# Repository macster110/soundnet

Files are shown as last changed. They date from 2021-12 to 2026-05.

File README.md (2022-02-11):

  

# SoundNet                                            

## Introduction

Bycatch (accidental entanglement in fishing gear) is by far the greatest cause of anthropogenic mortality in toothed whales (sperm whales, dolphins, porpoise, beaked whales and river dolphins), with hundreds of thousands estimated killed each year. This enormous mortality means bycatch is an acute welfare and conservation issue which has led to large population declines and the likely extinction of at least one species and possibly two others in the near future (vaquita and Maui’s dolphin). Despite bycatch being one of the top conservation concerns for many toothed whale species, we do not know why seemingly highly intelligent animals with sophisticated sensory abilities get entangled in nets.

The reason for this knowledge gap is primarily because it's very difficult to study behaviour underwater. Video cameras cannot see more than a few meters and tagging dolphins and porpoises is very difficult and may not provide the required data. However, all toothed whales studied so far produce echolocation clicks to hunt and sense their surroundings. These clicks (and other sounds) can be detected on acoustic recorders allowing large areas of the ocean to be monitored. Whilst passive acoustic monitoring (PAM) is oten used to detect the presence and classify the species of toothed whales in an area, in certain configurations acoustic recorder can also be used to localise the position of animals. 

SoundNet is an open-source hardware and software system for localising the position of dolphins and porpoises around fishing gear, particularly focussed on gill nets (which cause the most bycatch by far). It allows dolphins and porpoises to be tracked in 3D around nets allowing both their movement and acoustic behaviour to be studied and providing insights into how animals interact with nights (and thus provide some explanation on how they might become entangled). SoundNet can be deployed from almost any fishing vessel and this provides a powerful and highly practical tool for studying the beahviour of toothed whales. 

## Concept 

SoundNet has a relatively simple concept. Two recorders which can work out the geo-referenced bearing to a received click are deployed on the headline of gill net separated by 20-50m. If two devices detect the same click, then the point at which the bearings cross is the position of the animal (see Figure 1). 

<p align="center">
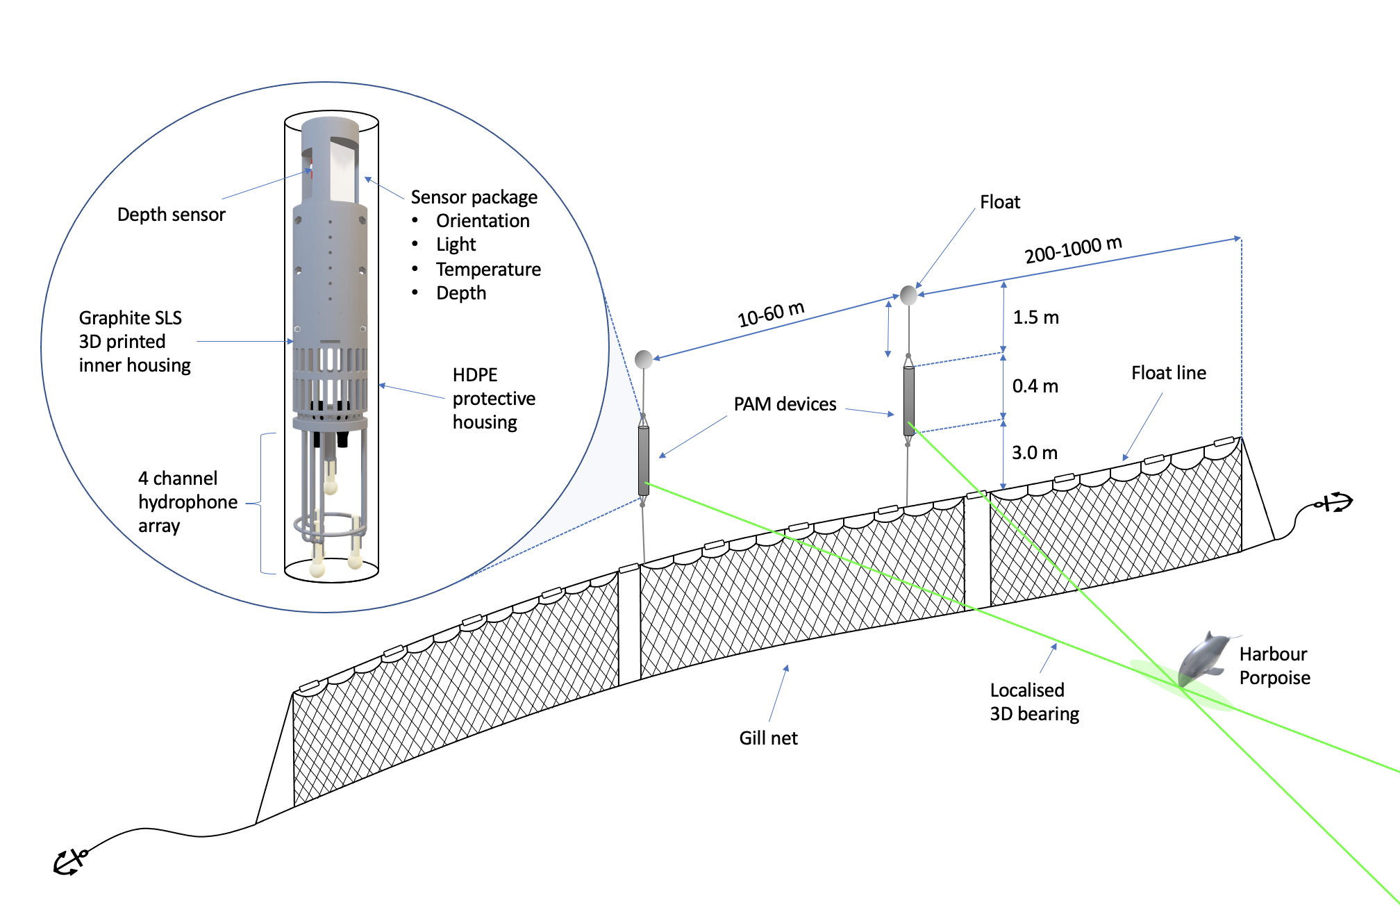
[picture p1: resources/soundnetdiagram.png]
  
</p>

_Figure 1. Diagram of the localising array (not to scale). Two recording devices were attached to the floatline of a gill net via a 3 m strop line. The recording devices were kept slightly positively buoyant using a small float, allowing them to maintain position in the water column above the float line without deforming the net. Each device contained a tetrahedral 4 element hydrophone cluster which enabled the calculation of 3D localisation vector to the source of a received sound. As a given deployment involved two devices, there was effectively an 8-channel hydrophone array mounted on the net. If both devices detected the same click, the point at which the two vectors intersected indicated the instantaneous 3D location of the animal. Animal movement patterns could then be inferred by interpolating these 3D locations._

However, whilst the concept is straightforward the implementation requires several components. 

1)	A recorder which can work out a bearing to a receiver requires multiple synchronised hydrophones. The system is based on a 4 channel SoundTrap which can be ordered from www.oceaninstrument.com. The housing section of the repository contains designs to 3D print a housing which attaches the SoundTrap and holds 4 hydrophones in a tetrahedral configuration
2)	Although multiple hydrophones can provide a bearing to an animal, the bearing needs to be georeferenced (i.e. referenced from north) for acoustic localisation to be possible. This requires an additional sensor packaged which attaches to the rear port of the SoundTrap and provides accurate 3D orientation, depth, temperature and light measurements. The sensor package section provides housing, electronic and firmware for the sensor package.
3)	Although bearings are a good way to conceptualise how the system works, they are not a great way to localise animals positions. A localization algorithm based on time delay measurements between the hydrophones and a particle filter provides much more accurate 3D tracks. The software workflow to analyse the acoustic data from SoundNet devices is detail in the analysis section.  

## Data

The resulting data from a successfully deployed system and analysis provides 3D tracks of animals which can be cross referenced with acoustic behaviour, for example tell-tale foraging buzzes. Figure 2 shows an example of 3D tracks of harbour porpoises around the net. 

<p align="center">
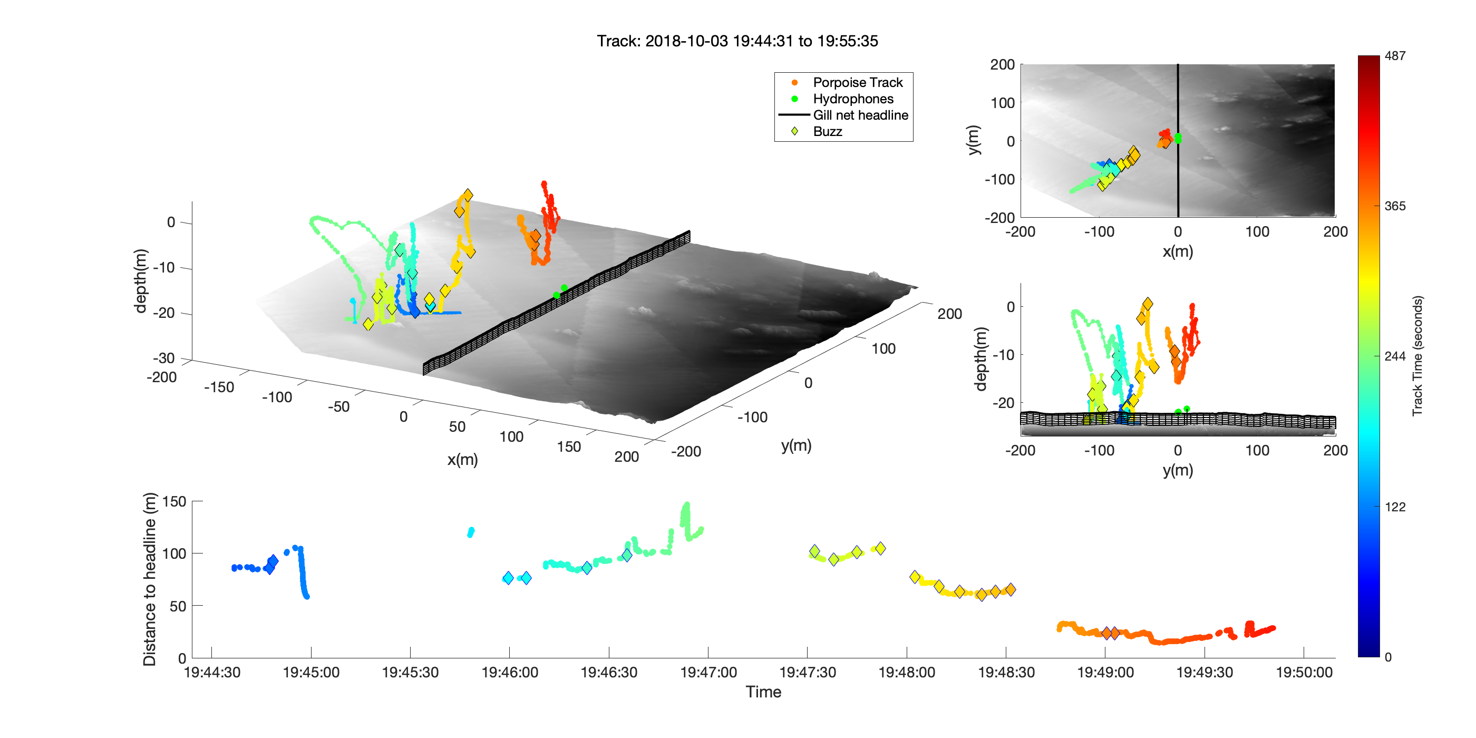
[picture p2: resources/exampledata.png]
  
</p
  
_Figure 2. Example of a 3D dive track of a single harbour porpoise where the porpoise approaches but does not come within 5 m of the gill net. A) A 3D view of the track, including bathymetry and the position of the gill net (black). Note that the gill net was assumed to be in line with the recording devices and  2m above the seabed.   B) A top-down view, and C) the depth profile along the gill net. . In this example, the porpoise dives close to the net several times producing foraging buzzes (or possibly calls) throughout the water column and towards the end of the encounter comes very close (< 5 m) to the net._

## License

This project is fully open source and any component can be used by anyone as long as it’s credited properly. We provide no guarantees and may not provide support without prior agreement.

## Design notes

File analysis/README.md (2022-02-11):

# Acoustic Analysis

SoundNet data consist of two or more (if more devices are used) sets of 4 channel wave files and sensor package files. 

## Acoustic data

### Analysis in PAMGuard

The acoustic data is analysed in PAMGuard to detect and classify possible porpoise clicks. A manual analyst then verifies detections using PAMGuard's manual annotation tools to mark out click trains and remove spurious detections (e.g. echoes). Detected clicks along with metadata such as bearing and time delays are saved to bespoke PAMGaurd files (PAMGaurd binary files) which can be imported into MATLAB using the [MATLAB to PAMGuard library](https://github.com/PAMGuard/PAMGuardMatlab) (note: you must download this library and add it to your MATLAB path). 

<p align="center">
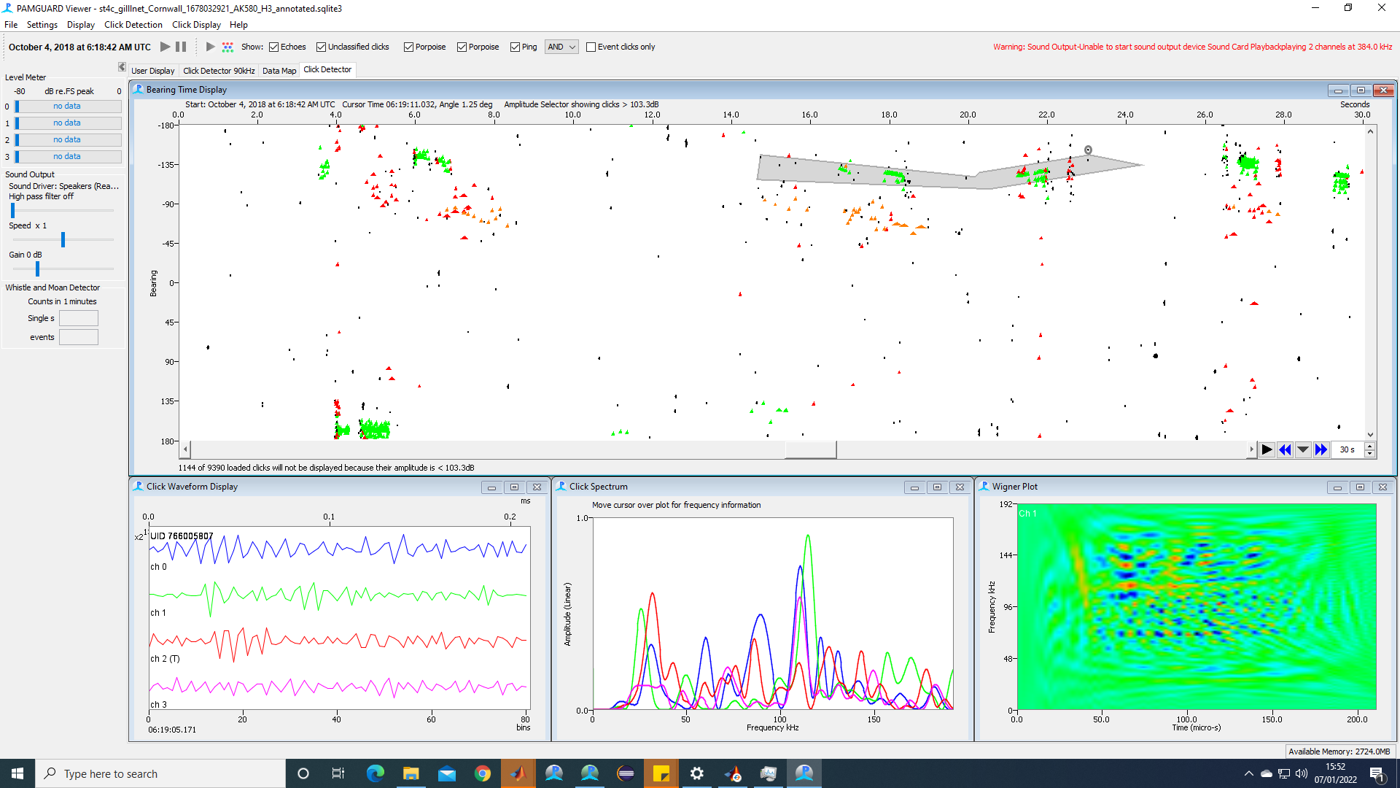
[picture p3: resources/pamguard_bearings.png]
  
</p>

_An example of clicks detected on one SoundNet device. PAMGuard automatically matched clicks on different hydrophones (on the same device, not between devices) and calculated the time delays, horizontal and vertical bearings. A manual analyst can use the slowly changes bearings to mark out click trains in the bearing time display. If more than one animal is present there will usually be concurrent separated bearing tracks._ 

### PAMGuard MATLAB library

Opening a PAMGuard binary file is straightforward. For example, a folder of binary files can be opened via

```Matlab
%the folder
folder = 'rootpath\mypamguardfolder'; 

% load clicks
clicks = loadPamguardBinaryFolder(folder, 'Click_Detector_Clicks_*.pgdf', 5);
```
This will return an array of clicks, with each element a structure containing metadata for each click such as time, waveform, time delays, bearings (if multiple hydrophones). The data can be explored in MATLAB's variable explorer or accessed via code. For example, to extract the time delay values from the first clicks in the array use 

```Matlab
timedelays = clicks(1).delays
````
The time delays are measured between all hydrophones - so for four hydrophones there are six measurements - i.e. the time delays between channels 0 - 1,  0 - 2,  0 - 3,  1 - 2,  1 - 3 and 2 - 3. 

Waveforms from a click detection can be plotted using 

```Matlab
%waveform of the first click 
wave = clicks(1).wave

tiledlayout(1,clicks(1).nChan)
for i = 1:nChan
  nexttile
  plot(wave); 
  ylabel('Amplitude (linear)')
  xlabel('Time (bins)')
end
````

<p align="center">
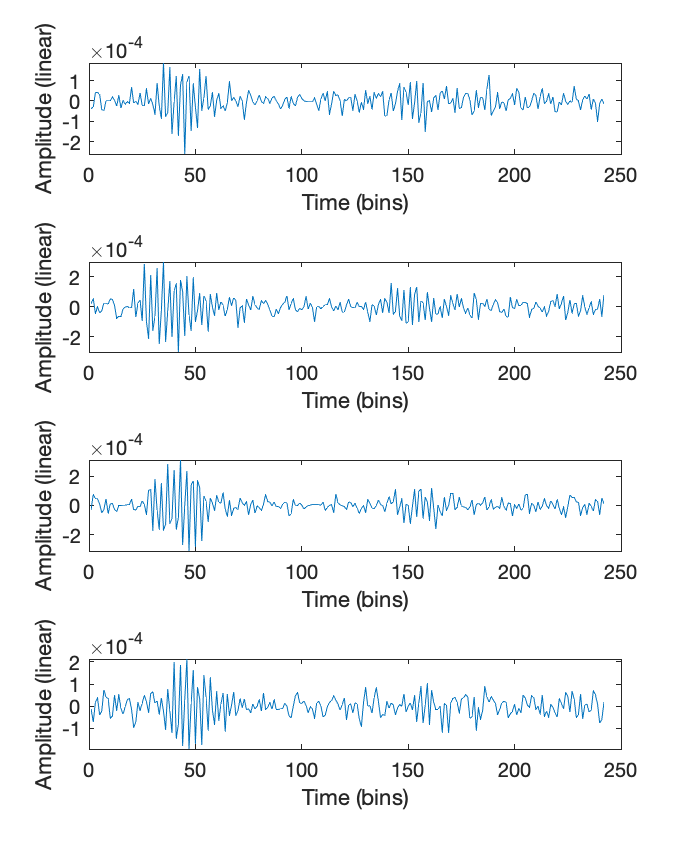
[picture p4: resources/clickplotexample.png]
  
</p>

_An example of waveforms from a single click detection imported from PAMGuard and plotted using MATLAB. Note that PAMGuard automatically matched click between hydrophones within the same SoundNet device and so one click detection contains 4 waveforms. PAMGuard also calculates the time delays between the waveforms and localised the horizontal and vertical bearing for each click_

Note that there is also a [comprehensive R library](https://github.com/TaikiSan21/PamBinaries) for PAMGuard which has like-for-like functions to the MATLAB library. 

### Importing datasets

The matlab library has several convenience functions for importing large datasets. For example,

```Matlab
% load clicks from a folder
% binaryfolder - path to the folder containinn PAMGuard binary files
clicks = loadPamguardBinaryFolder(binaryfolder, 'Click_Detector_Clicks_*.pgdf', 5);
```
will load clicks from a folder of binary files and 

```Matlab
% sqlLite_dB - path to PAMGuard's database
% binaryfolder - path to the folder containinn PAMGuard binary files
click_events = load_event_clicks( sqlLite_dB, binaryfolder)
```

will load manually annotated clicks marked out in the click detector module. 

## Sensor files

Sensor files from the sensor package attached to the SoundTrap are human readable .csv files which are saved to the SoundTrap's SD card. These can be opened using the MATLAB code in the sensor package folder. For example, to open a folder of sensor files and plot the data use

```Matlab
%folder where the csv files are located. 
folder = 'rootpath\mysensorfolder'; 

% convert csv files to one matlab struct
[sensordata] = sensorcsv2mat(csvfolder);

%plot the sensor data
plot_sensor_data(sensordataStruct); 
```

The sensordata struct contains the output from the orientation, depth, temperature, light and battery sensors on the sensor package 

<p align="center">
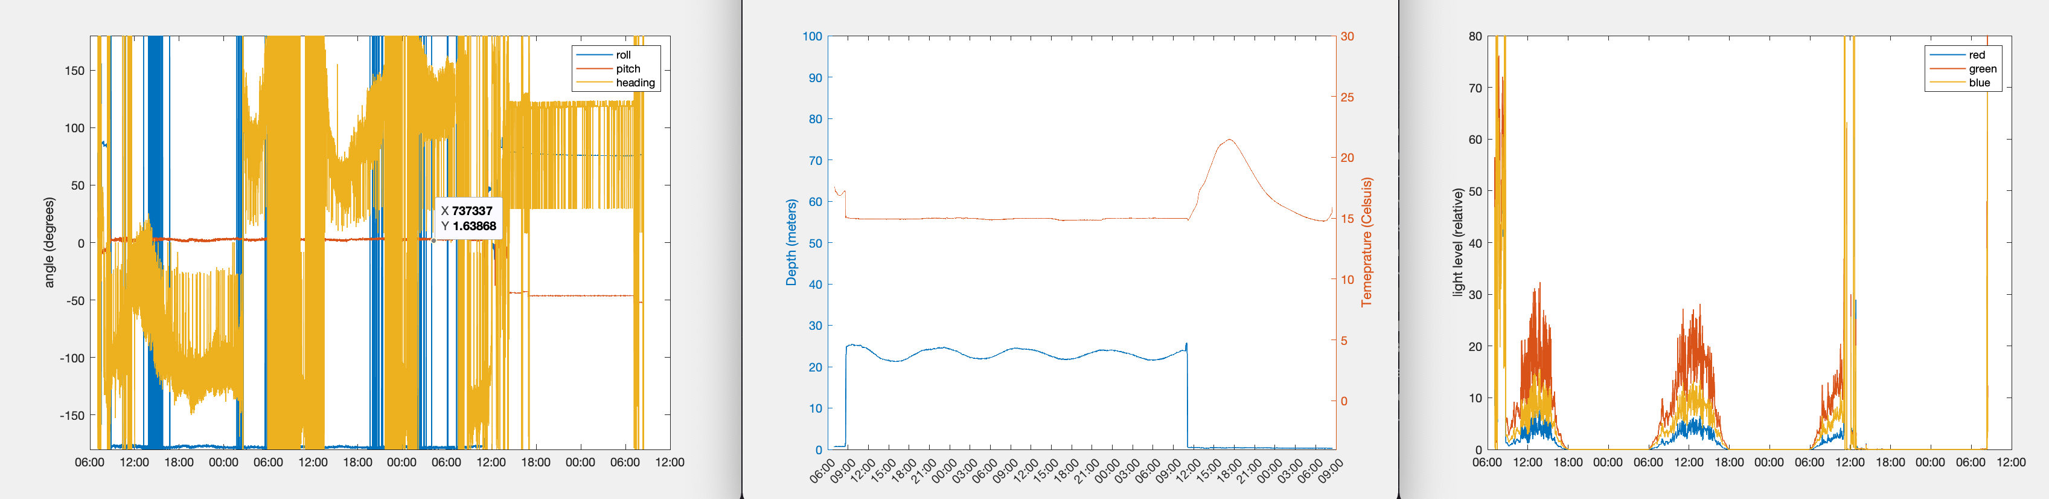
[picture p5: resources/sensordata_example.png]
  
</p>

_Example of sensor package data plotted in MATLAB._

## Geo referencing hydrophones and/or localised bearings

The sensor data is used to geo-reference clicks. The _sensordata_ folder imports .csv files and concatonates the sensor data into a single matlab structure. The functions in the _georef_ folder then combine imported click detections and the sensordata to provide geo-referenced bearings and/or hydrophone positions. aan example of how to use the functions is shown in _georef/georef_example.m_

<p align="center">
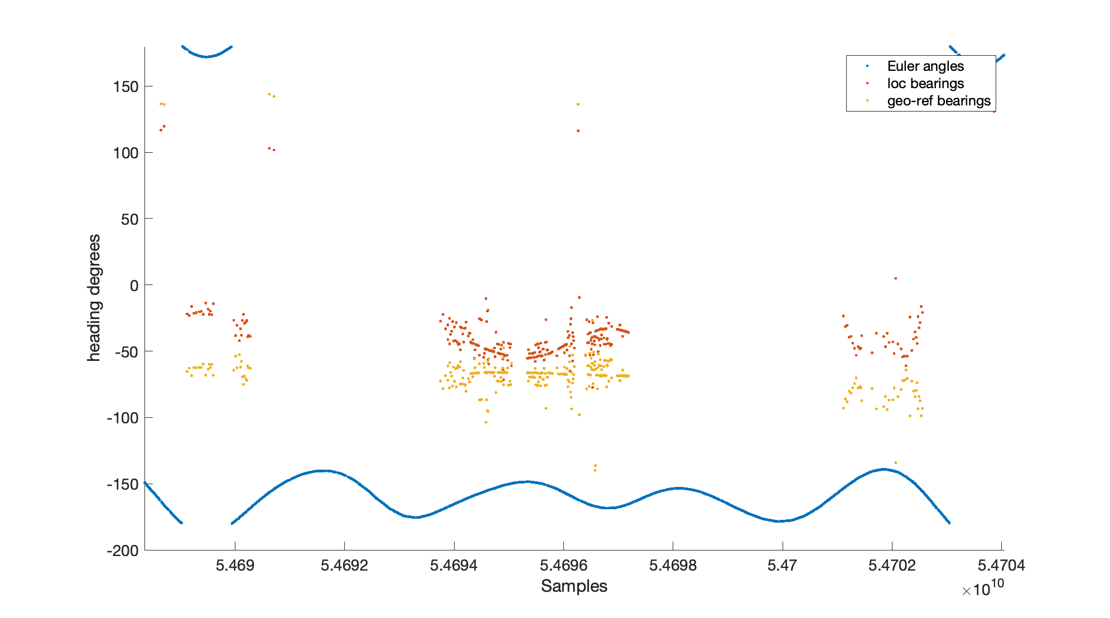
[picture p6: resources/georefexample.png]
  
</p>

_A plot of raw and georeferenced bearings to detected porpoise clicks alongisde the heading data recorded on the sensor package._

## Localisation

Localisation is performed using a particle filter. A particle filter in this context works by updated the position of a set of particles upon the detection of a click on one or more recording devices. The particles are updated based on the position of the hydrophones, the received time delays and movement model of a harbour porpoise. In this way localisation is not based on single clicks but instead on the evolved state of click trains, allowing more accurate animal tracks t be determined.

The generalised particle filter code is based on a script by  _Diego Andrés Alvarez Marín (2022). Particle filter tutorial (https://www.mathworks.com/matlabcentral/fileexchange/35468-particle-filter-tutorial), MATLAB Central File Exchange._

example_porpoise.m demonstrates how the particle filter is used in an acoustic localisation context. The script generates a simulated porpoise track, determine the time delays for clicks produced along the track and then localises the simulated track using a particle filter. 

<p align="center">
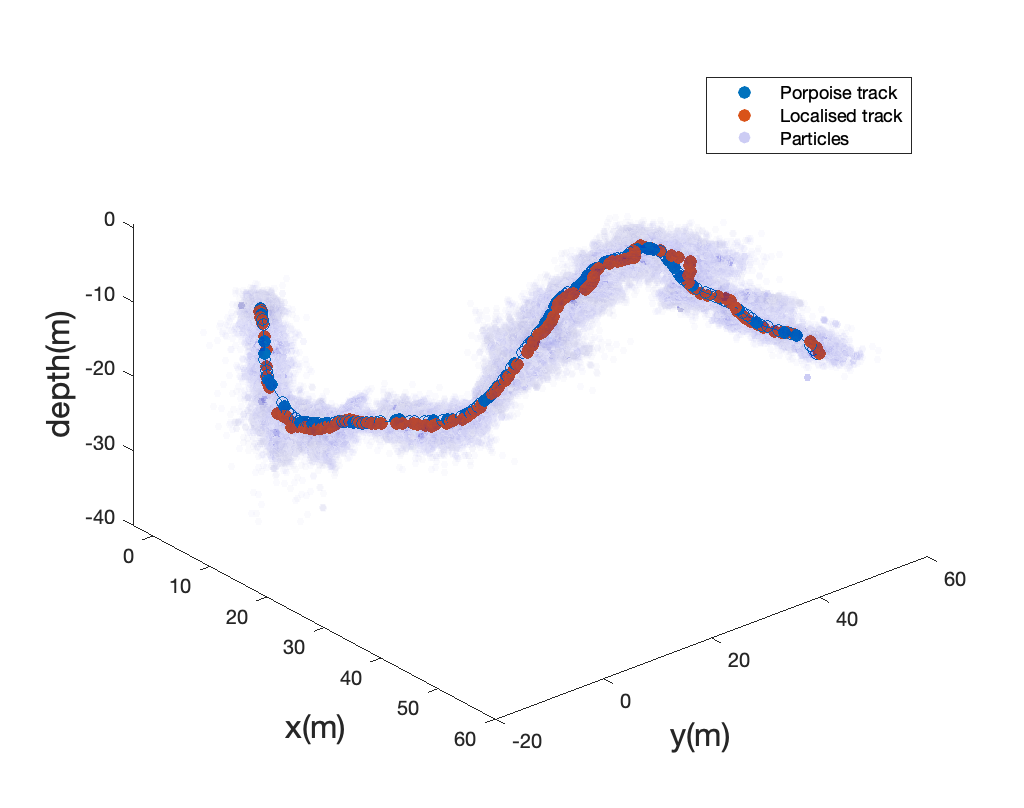
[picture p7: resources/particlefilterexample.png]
  
</p>

_Results of the particle filter using the porpoise_example.m script. The orange points are the localised positions and the blue dots the simulated animal track. The cloud of translucent points are the individual particles used by the sequential Monte Carlo process. The mean location of particles is the position of the animal and the distribution of particles is an estimate of the likely uncertainty. For example the distribution of particles in the x,y or z dimensions represents the likely error of the localisation in  x,y and z respectively._

## Data management

Data management will vary depending on the project and thus data management code is not provided here; the code provided and associated help should be considered a toolbox to construct an acoustic workflow for localisation, rather than a one-stop solution. 

However, whilst each acoustic workflow will depend on the study site, species of interest etc., they will all require some general stages as follows. 

1) Extract sounds of interest.
3) Geo reference hydrophone positons using the sensor package data.
4) Time align the SoundTraps and match clicks between different devices. 
5) Pass time aligned and geo-referenced data to the localisation algorithm to determine animal tracks.

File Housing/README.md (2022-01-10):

# Housing

Each SoundNet device consists of a 4 channel SoundTrap, a sensor pacakage and an outer housing which holds the hydrophones and sensor package in place. The outer housing is made up of three 3D printed parts which fit together over the SoundTrap and sensor package and kept in place with stainless steel bolts. 

<p align="center">
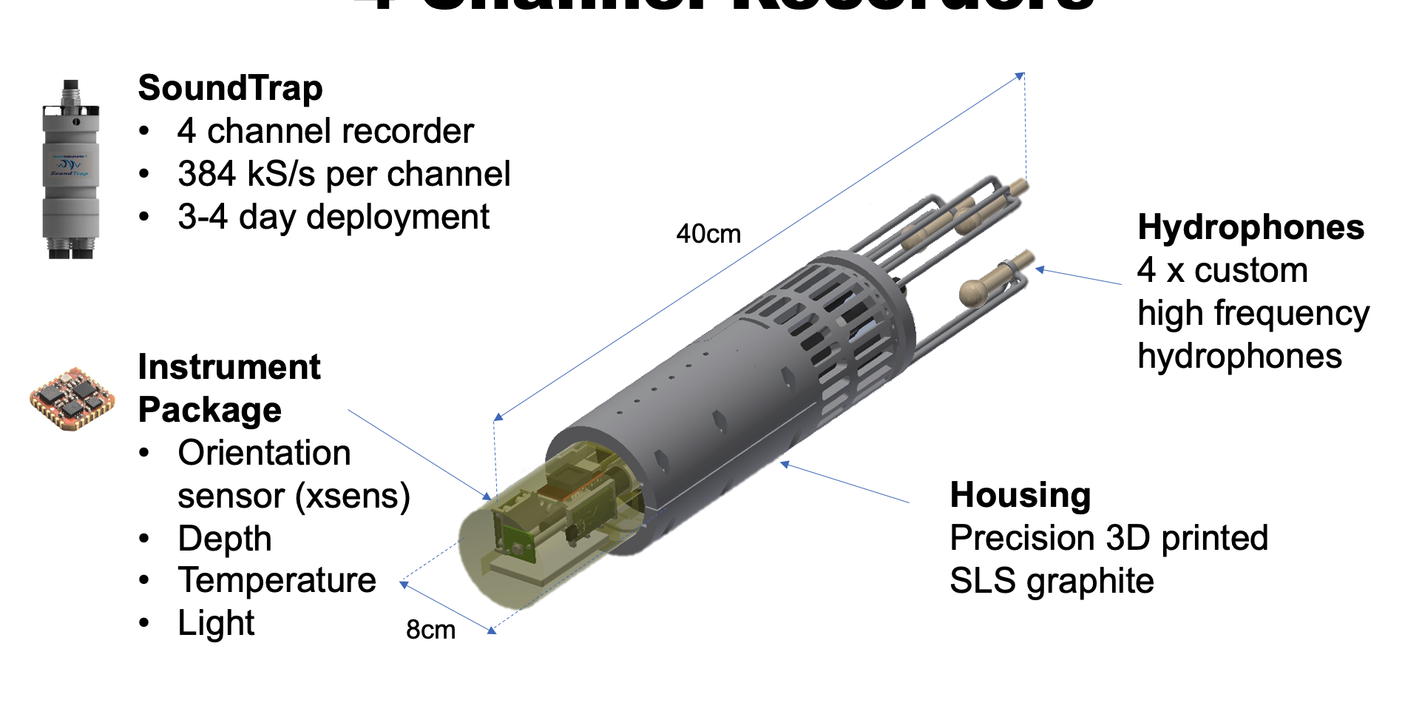
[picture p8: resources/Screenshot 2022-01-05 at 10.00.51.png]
  
</p>

_Diagram of a SoundNet device. The 3D printed housing fits over the 4 channel SoundTrap and is kept in place by stainless steel bolts._

The three .stl files here can be 3D printed easily on a local printer or using a service. The material should be rated for the marine environment and should be suitable for the intricate construction of the hydrophone frame.

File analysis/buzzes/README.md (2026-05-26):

# Buzz and call analysis 

## Importing annotated buzzes and calls
Buzz and communication call analysis was conducted by marking out rapid click sequences with an ICI <40 ms in PAMGuard. The click events were then imported into PAMGuard using the `load_event_clicks` function (Note this requires the [PAMGuard MATLAB library](https://github.com/PAMGuard/PAMGuardMatlab/releases)). 

## Plotting buzz and call contours

Once the buzzes have been imported into MATLAB, they can be saved as .mat files within the MATLAB IDE. The two .mat files for each recording device used for our analysis are included (`st13_buzzes.mat` and `st16_buzzes.mat`). Each structure contains an event and a list of click structures for each annotated click sequence in PAMGuard's standard format. More information and a tutorial on this can be found [here](https://www.pamguard.org/tutorials/matlabrpython.html); 

Once the annotated rapid click sequences have been imported into MATLAB, there are various functions which convert the structures into ICI (inter-click interval) contours that can be used in further analysis. 

### Functions

The first stage in analysis is to load the buzzes 

```matlab
st13buzzes = load(fullfile(getsuperfolder, '/2016-20 Gill nets/SoundTrap_4c/20191114_Cornwall_AK627_H3/buzzes/st13_buzzes.mat'));
st16buzzes = load(fullfile(getsuperfolder, '/2016-20 Gill nets/SoundTrap_4c/20191114_Cornwall_AK627_H3/buzzes/st16_buzzes.mat'));
```

Then, depending on what analysis is being performed, it may be necessary to filter buzzes by quality.

```matlab
minq = 3; %minimum quality for buzzes. 1 for the best buzzes, 2 for the best and medium and 3 for all buzzes.

% bycatchdate = datenum('14-Nov-2019 12:55:00');

buzzesst{1} = filtbuzzesQ(st13buzzes.buzzes, minq);
buzzesst{2} = filtbuzzesQ(st16buzzes.buzzes, minq);
```

Once the potential buzzes have been identified, it is necessary to match them across the two recording devices, extracting the "best" buzz from each device (i.e. the pone with the most clicks and highest signal-to-noise ratio). 

```matlab
[buzzes_combined] = combinemultibuzz(buzzesst);
```

The buzzes are still in PAMGuard's standard format; however, this is a complicated format and includes large amounts of metadata not required for onward analysis. To simplify, buzzes can be converted to ICI contours. These sometimes have spikes due to missed clicks and jitter due to timing recording in PAMGuard - a spike removal and smoothing algorithm is therefore often required to remove spurious data points. 

```matlab
for i=1:length(buzzes_combined)

    abuzz = buzzes_combined(i);

	%convert to ici
    [ici, timesec, buzzmetrics] = buzz2ici(abuzz); 

	%remove spikes due to missed clicks
    smoothici = removeicispikes(ici, 3, 5);

	%smooth using in built matlab smooth fucntion
    smoothici = smooth(smoothici);

	icibuzz(i).ici = smoothici

end 
```

Buzzes and calls are now ready to be plotted. The code below shows an example on of plotting buzzes. 

```matlab
%Plot the buzz contours before and after the bycatch even on the same plot
%and compare to Sorensen 2018.

% load the buzz contours
clear
close all

minq = 3; %minimum quality for buzzes. 1 for the best buzzes, 2 for the best and medium and 3 for all buzzes.
maxamp = 105; % filter out the lowest amplitude clicks whihc are almost always noise dB re 1uPa pp. 
maxici = 0.040;%the maximum ICI to allow in seconds

%define the times between the stages of the bycatch events. 
[bycatch,bycatchevent, bycatcheventext] = getbycatchtime();
timelims = {
    [bycatcheventext(1), bycatch(1)],
    [bycatch(1), bycatch(2)],
    [bycatch(2), bycatcheventext(2)]
    };

%load all buzzes.
st13buzzes = load(fullfile(getsuperfolder, '/2016-20 Gill nets/SoundTrap_4c/20191114_Cornwall_AK627_H3/buzzes/st13_buzzes.mat'));
st16buzzes = load(fullfile(getsuperfolder, '/2016-20 Gill nets/SoundTrap_4c/20191114_Cornwall_AK627_H3/buzzes/st16_buzzes.mat'));

% bycatchdate = datenum('14-Nov-2019 12:55:00');

buzzesst{1} = filtbuzzesQ(st13buzzes.buzzes, minq);
buzzesst{2}  = filtbuzzesQ(st16buzzes.buzzes, minq);

[buzzes_combined] = matchbuzzes(buzzesst, 1);

%create on list of buzzes
for i=1:length(buzzes_combined)
    nbuzzes=[];
    for j=1:length(  buzzes_combined(i).buzz_multi)
        if (~isempty(buzzes_combined(i).buzz_multi(j)))
            nbuzzes(j) = length(buzzes_combined(i).buzz_multi(j).clicks);
        else
            nbuzzes(j) = 0 ;
        end
    end

    [~, index] = max(nbuzzes);
    buzzes(i) = buzzes_combined(i).buzz_multi(index);
end
hold on

cols = getdefaultcols;

subplot(1,7,7)
[foragingbuzz, communicationbuzz] = get_Sorensen_buzz_ICI();

ici_millisc = 1000*( 10.^communicationbuzz(:,1));
ici_millisf = 1000*( 10.^foragingbuzz(:,1));

hold on
plot(communicationbuzz(:,2), ici_millisc, 'LineWidth', 2);
plot(foragingbuzz(:,2), ici_millisf, 'LineWidth', 2);
hold off
l=legend('Communication call', 'Foraging buzz');
l.FontSize = 12;
ylabel('ICI (ms)')
xlabel('p')
ylim([0,maxici*1000])
set(gca, 'FontSize', 14)

alpha = 0.2;
for jj=1:length(timelims)
    %select the correct subplot
    subplot(subplot(1,7,[2*jj-1, 2*jj]));
    for i = 1:length(buzzes)

        abuzz = buzzes(i).clicks;

        if ~(buzzes(i).date>timelims{jj}(1) && buzzes(i).date<timelims{jj}(2))
            %buzz not within time limits
            continue;
        end

        %%calculate some buzz metrics.
        nclks(i) = length(buzzes(i).clicks);
        amplitudeclks = zeros(length(buzzes(i).clicks), 1);
        for j=1:length(buzzes(i).clicks)
            amplitudeclks(j) = max(buzzes(i).clicks(j).wave(:,1));
            amplitudeclks(j) = 20*log10(amplitudeclks(j))+170;
        end
        maxamps(i) = max(amplitudeclks);

        datetimesnum = [abuzz.startSample];

        [ici, timesec, buzzmetrics] = buzz2ici(buzzes(i)); 

        % timesec = (datetimesnum-min(datetimesnum))/384000;
        % timesec=sort(timesec);
        % timesec=timesec(1:end-1);
        % 
        % % index = diff(timesec)<maxici;
        % % timesec=timesec(index);
        % 
        % ici = diff(timesec);

        medianici = median(ici);
        meanici = mean(ici);

        if nclks(i)>20 && maxamps(i)>maxamp && medianici<maxici
    
             %may want to keep spikes asalgorithm isn't great for low SNR quality calls   
            %smoothici = removeicispikes(ici, 3, 5);
            
            smoothici = smooth(smoothici);

            % clf
            % hold on
            hold on
            n=1;
            ii=1;
            plotici = [];
            while ii<length(timesec)
                if (smoothici(ii)<maxici && smoothici(ii)<3*medianici)
                    plotici(n,2) = smoothici(ii);
                    plotici(n,1) = timesec(ii);
                    n=n+1;
                else
                    if (length(plotici)>5)
                        plot(plotici(:,1), 1000*plotici(:,2), 'LineWidth', 2,'Color', [cols(1,:), alpha])
                    end
                    n=1;
                    plotici=[];
                end
                ii=ii+1;
            end

            if (length(plotici)>5)
                plot(plotici(:,1), 1000*plotici(:,2), 'LineWidth', 2,'Color', [cols(1,:), alpha])
            end

            % scatter(timesec(1:end-1), 1000*smoothici, '.')
            title(num2str(buzzes(i).event_id))
            ylim([0,maxici*1000])
            drawnow
        end

        xlim([0,2])
        ylim([0,maxici*1000]);
        xlabel('Time (s)')
        set(gca, 'FontSize', 14)

    end
end

%%now let's finish the plots off
subplot(1,7,[3,4]);
title("During bycatch event")

subplot(1,7,[1,2]);
title("Before bycatch event")
ylabel('ICI (ms)')

subplot(1,7,[5,6]);
title("After bycatch event")

l.FontSize=12;
```

<p align="center">
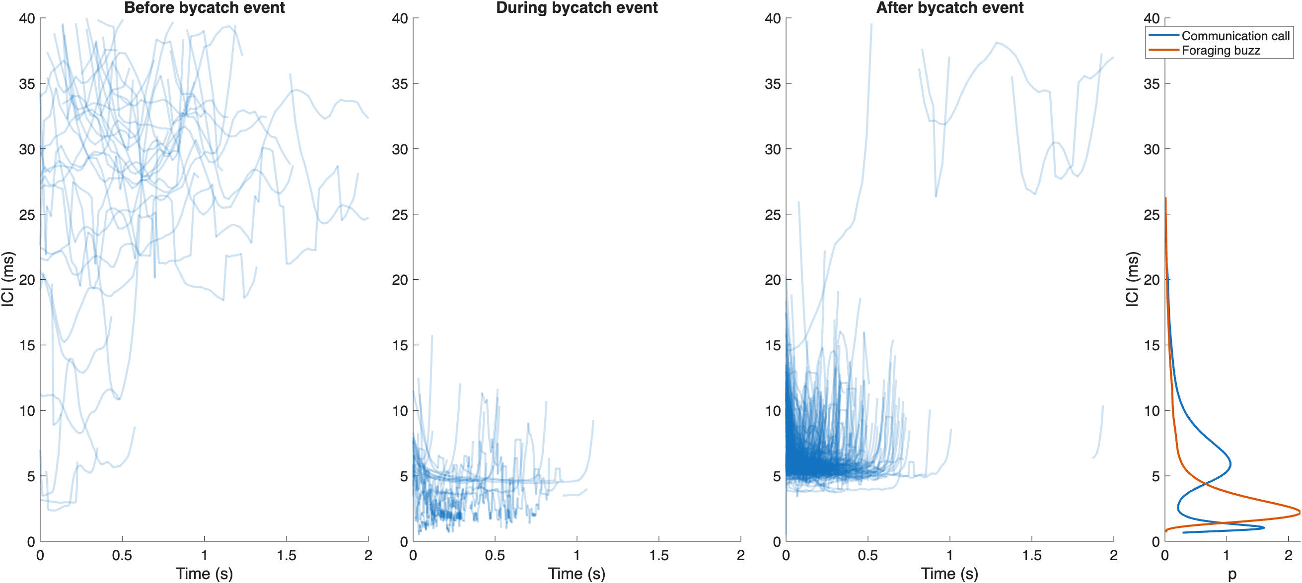
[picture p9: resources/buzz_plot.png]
  
</p>

_Rapid sequences of clicks (either foraging approaches/buzzes or calls) plotted alongside the inter-click interval distributions for communication calls and foraging buzzes from DTAG data analysis  (Sørensen et al., 2018) before, during and after the bycatch occurs._

Sørensen, P.M. et al. (2018) ‘Click communication in wild harbour porpoises (Phocoena phocoena)’, Scientific Reports, 8(1), p. 9702. Available at: https://doi.org/10.1038/s41598-018-28022-8.

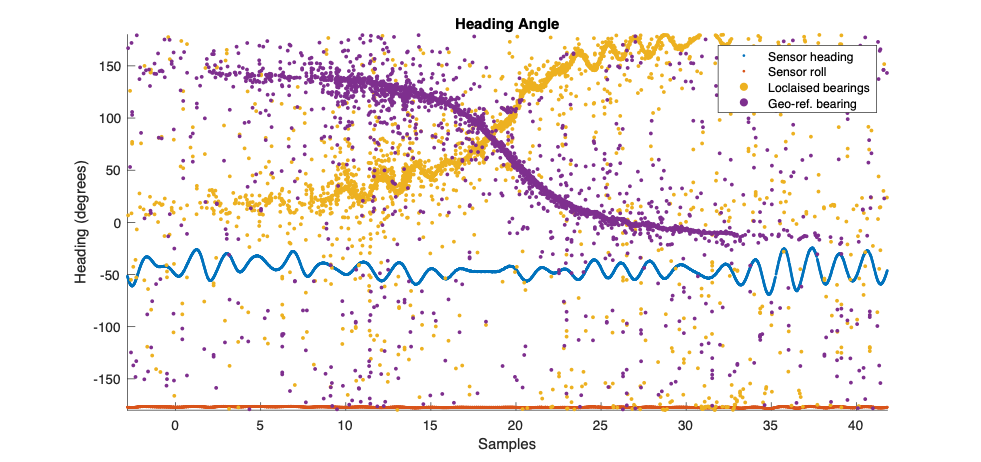
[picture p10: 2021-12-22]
resources/clkbearings_orient.png

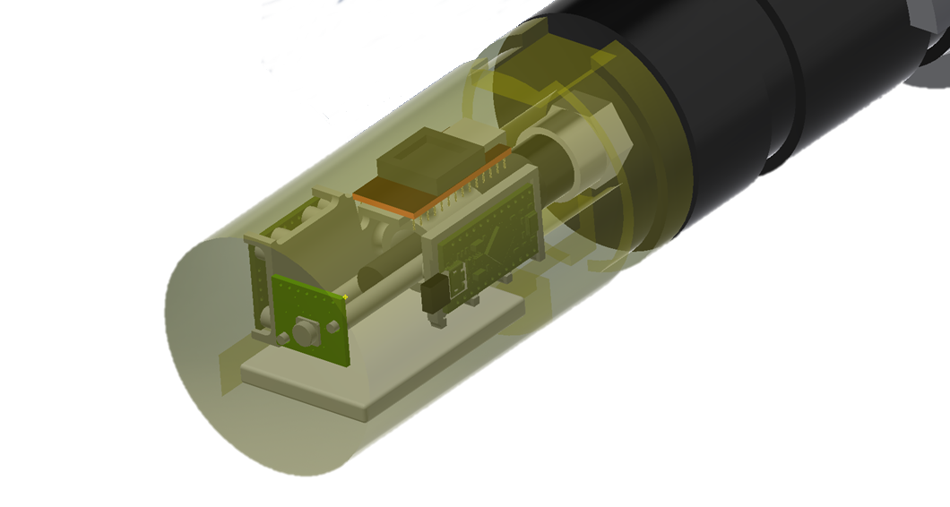
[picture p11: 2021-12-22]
resources/SoundTrapInstrument.png

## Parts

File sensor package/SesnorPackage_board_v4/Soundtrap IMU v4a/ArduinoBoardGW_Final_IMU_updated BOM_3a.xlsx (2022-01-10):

Do Not Populate | Part | Value | Device | Package | Description | OC_FARNELL
 | C1 | 0.1uF | CAP0603-CAP | 0603-CAP | Capacitor 5% tolerence
 | C3 | 0.1uF | CAP0603-CAP | 0603-CAP | Capacitor 5% tolerence
 | C5 | 1uF | CAP0603-CAP | 0603-CAP | Capacitor 5% tolerence
 | C6 | 1uF | CAP0603-CAP | 0603-CAP | Capacitor 5% tolerence
 | C7 | 4.7uF | CAP0402-CAP | 0402-CAP | Capacitor 5% tolerence
 | C8 | 4.7uF | CAP0402-CAP | 0402-CAP | Capacitor 5% tolerence
 | C9 | 0.1uF | 0.1UF-25V(+80/-20%)(0603) | 0603-CAP | CAP-00810
 | C10 | 1uF | CAP0603-CAP | 0603-CAP | Capacitor 5% tolerence
 | C11 | 0.1uF | CAP0402-CAP | 0402-CAP | Capacitor 5% tolerence
 | C12 | 1uF | CAP0402-CAP | 0402-CAP | Capacitor 5% tolerence
 | C13 | 10uF | CAP_POL1206 | EIA3216 | Capacitor Polarized, ESR 0.9ohm, 10V, 10% | http://uk.farnell.com/avx/tpsa106k010r0900/cap-tant-10uf-10v-case-a/dp/1432565
 | C14 | 10nF | CAP0402-CAP | 0402-CAP | Capacitor 5% tolerence
 | C19 | 10uF | CAP_POL1206 | EIA3216 | Capacitor Polarized, ESR 0.9ohm, 10V, 10% | http://uk.farnell.com/avx/tpsa106k010r0900/cap-tant-10uf-10v-case-a/dp/1432565
 | D1 | Yellow | LED0603 | LED-0603 | LEDs | https://www.digikey.co.uk/product-detail/en/osram-opto-semiconductors-inc/LO-L29K-H2L1-24-Z/475-2481-1-ND/1802608
 | D3 | Green | LED0603 | LED-0603 | LEDs | https://www.digikey.co.uk/product-detail/en/kingbright/APHD1608LCGCK/754-2031-1-ND/7043085
 | D11 | RED | LED0603 | LED-0603 | LEDs | https://www.digikey.co.uk/product-detail/en/vishay-semiconductor-opto-division/TLMS1000-GS08/TLMS1000-GS08CT-ND/4743829
 | D20 | Green | LED0603 | LED-0603 | LEDs | https://www.digikey.co.uk/product-detail/en/kingbright/APHD1608LCGCK/754-2031-1-ND/7043085
x | JP1 |  | PINHD-2X3 | 2X03 | 2x3 HEADER, .100" PITCH (RS Pro W82106T3825RC or similar)
x | P1 |  | SUBCON_MICRO_8_EDGE_ORDERED | SUBCON_MICRO_8_EDGE
x | P2 | MINI_IMU | MINI_IMU | MINI_IMU
x | P3 | EXT_PRES | EXT_PRES | EXT_PRES
x | P4 | LIPO | MOLEX 22-23-2021 | 22-23-2021 | .100 (2.54mm) Center Header - 2 Pin" | 1462926
 | Q1 | SW | INFINEON_BSS84P | SOT23 | p- channel -mosfet | http://uk.farnell.com/infineon/bss84ph6327xtsa2/mosfet-p-60v-0-17a-sot-23/dp/1056526?st=BSS84P
x | R |  | 1
 | R1 | 2K | RESISTOR0402-RES | 0402-RES | Resistor
 | R2 | 10K | RESISTOR0603-RES | 0603-RES | Resistor
 | R3 | 330 | RESISTOR0402-RES | 0402-RES | Resistor
 | R4 | 330 | RESISTOR0603-RES | 0603-RES | Resistor
 | R5 | 22 | RESISTOR0603-RES | 0603-RES | Resistor
 | R6 | 330 | RESISTOR0603-RES | 0603-RES | Resistor
 | R7 | 22 | RESISTOR0603-RES | 0603-RES | Resistor
 | R8 | 2.2k | 2.2KOHM1/10W1%(0603) | 0603-RES | RES-08272
 | R9 | 2.2k | 2.2KOHM1/10W1%(0603) | 0603-RES | RES-08272
 | R10 | 10K | 10KOHM1/10W1%(0603)0603 | 0603-RES | RES-00824
x | R11 | 220 | RESISTOR0402-RES | 0402-RES | Resistor
 | R12 | 10K | 10KOHM1/10W1%(0603)0603 | 0603-RES | RES-00824
 | R13 | 330 | RESISTOR0402-RES | 0402-RES | Resistor
 | R14 | 1k | RESISTOR0402-RES | 0402-RES | Resistor
 | R15 | 4.99k | R-US_R0603 | R0603 | RESISTOR | http://uk.farnell.com/bourns/cr0603-fx-4991elf/res-thick-film-4k99-1-0-1w-0603/dp/2787803
 | R16 | 4.99k | R-US_R0603 | R0603 | RESISTOR | http://uk.farnell.com/bourns/cr0603-fx-4991elf/res-thick-film-4k99-1-0-1w-0603/dp/2787803
 | R17 | 180 | RESISTOR0402-RES | 0402-RES | Resistor
 | R20 | 4.7k | RESISTOR0402-RES | 0402-RES | Resistor
 | R21 | 4.7k | RESISTOR0402-RES | 0402-RES | Resistor
x | SJ1 | IMU_PWR | SOLDERJUMPERNO | SJ_2S-NO | Solder Jumper
x | SJ2 | 3v3 | SOLDERJUMPERNO | SJ_2S-NO | Solder Jumper
x | T |  | 1
x | U$5 | D4 | TEST_POINT | TEST_POINT
x | U$6 | TEST_POINT | TEST_POINT | TEST_POINT
x | U$7 | TEST_POINT | TEST_POINT | TEST_POINT
x | U$8 | TEST_POINT | TEST_POINT | TEST_POINT
x | U$9 | TEST_POINT | TEST_POINT | TEST_POINT
x | U$10 | TEST_POINT | TEST_POINT | TEST_POINT
x | U$11 | TEST_POINT | TEST_POINT | TEST_POINT
x | U$12 | TEST_POINT | TEST_POINT | TEST_POINT
x | U$13 | TEST_POINT | TEST_POINT | TEST_POINT
 | U1 | MCP73831 | MCP73831 | SOT23-5 | Microchip's MCP73831 | 1332158
 | U2 | MIC5219 | V_REG_LDOSMD | SOT23-5 | Voltage Regulator LDO | 2510252
 | U3 | ATMEGA | ATMEGA32U4OUTFAKES | QFN-44-NOPAD_1:1-OUTFAKES | Atmel 44-pin 8-bit Microcontroller with 32KBytes of ISP Flash and USB Controller | 2425127
 | U4 | MAX1704X | MAX17042G+U | TDFN-8 | MAX17043/MAX17044: Battery Fuel Guage (43 is 1cell | https://www.mouser.co.uk/ProductDetail/Maxim-Integrated/MAX17043G%2bU
 | U5 | RS485SOIC | RS485SOIC | SO08 |  | 2067812
x | U6 | MS5803-14BA | MS5803-14BA | MS5803 |  | 2717379
 | U7 | XSENSE | XSENSE | MC-28PLCC-SMT |  | 2097220
 | U8 | ISL29125X | ISL29125IROZ-T7 | ODFN-6 | ISL29125 RGB Light sensor | https://www.mouser.co.uk/ProductDetail/Renesas-Intersil/ISL29125IROZ-T7?qs=8EBwJ8mibj2u1svZyuG5jQ%3D%3D
 | R18 | 100 | RESISTOR0603-RES | 0603-RES | Resistor
 | R19 | 10k | RESISTOR0603-RES | 0603-RES | Resistor
 | R22 | 10k | RESISTOR0603-RES | 0603-RES | Resistor
 | R23 | 10k | RESISTOR0603-RES | 0603-RES | Resistor
 | C2 | 0.1uF | CAP0603-CAP | 0603-CAP | Capacitor 5% tolerence
 | C4 | 0.1uF | CAP0603-CAP | 0603-CAP | Capacitor 5% tolerence

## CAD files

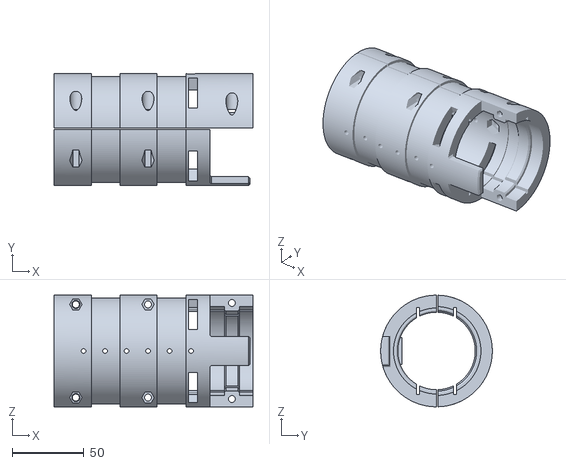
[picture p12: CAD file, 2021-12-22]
Housing/Trap frame with wider slots revE.stl
138.8 x 77.9 x 77.9

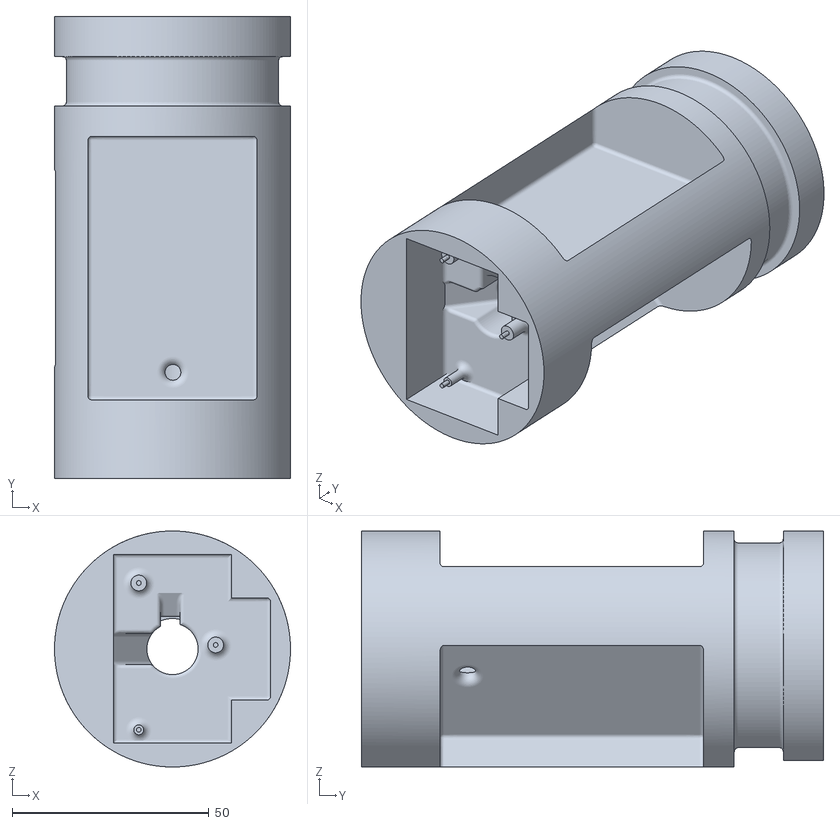
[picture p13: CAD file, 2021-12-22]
sensor package/positive model dual battery revD.stl
60.0 x 117.5 x 60.0

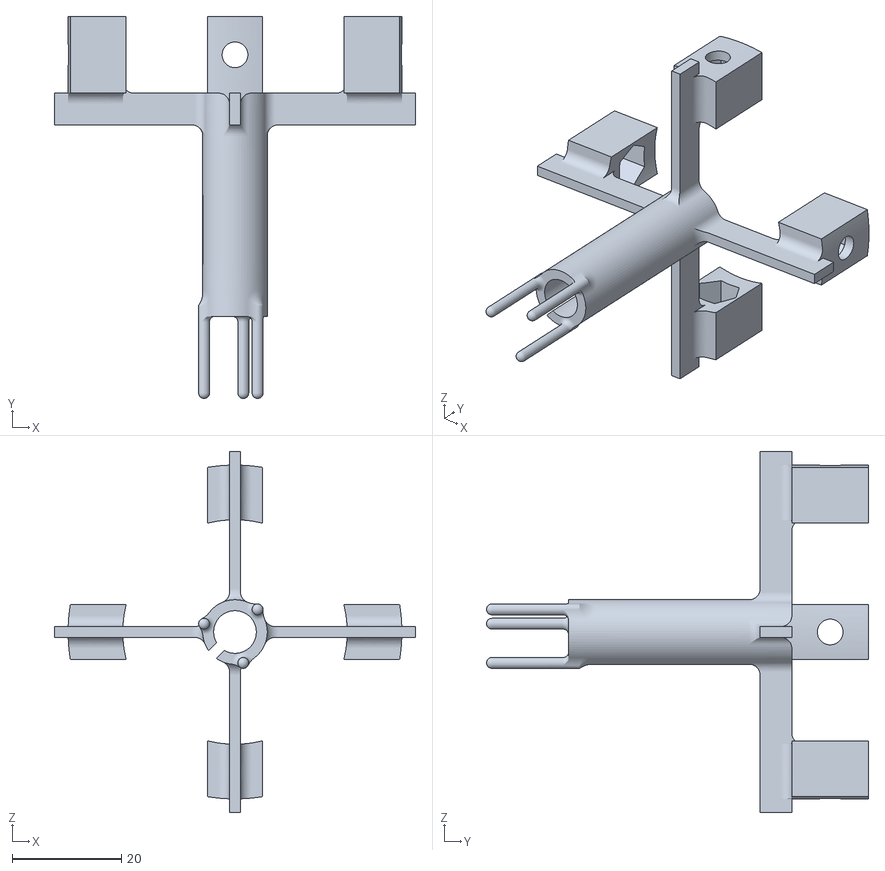
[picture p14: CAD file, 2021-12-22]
Housing/hydrophone brace revB.stl
66.0 x 69.8 x 66.0

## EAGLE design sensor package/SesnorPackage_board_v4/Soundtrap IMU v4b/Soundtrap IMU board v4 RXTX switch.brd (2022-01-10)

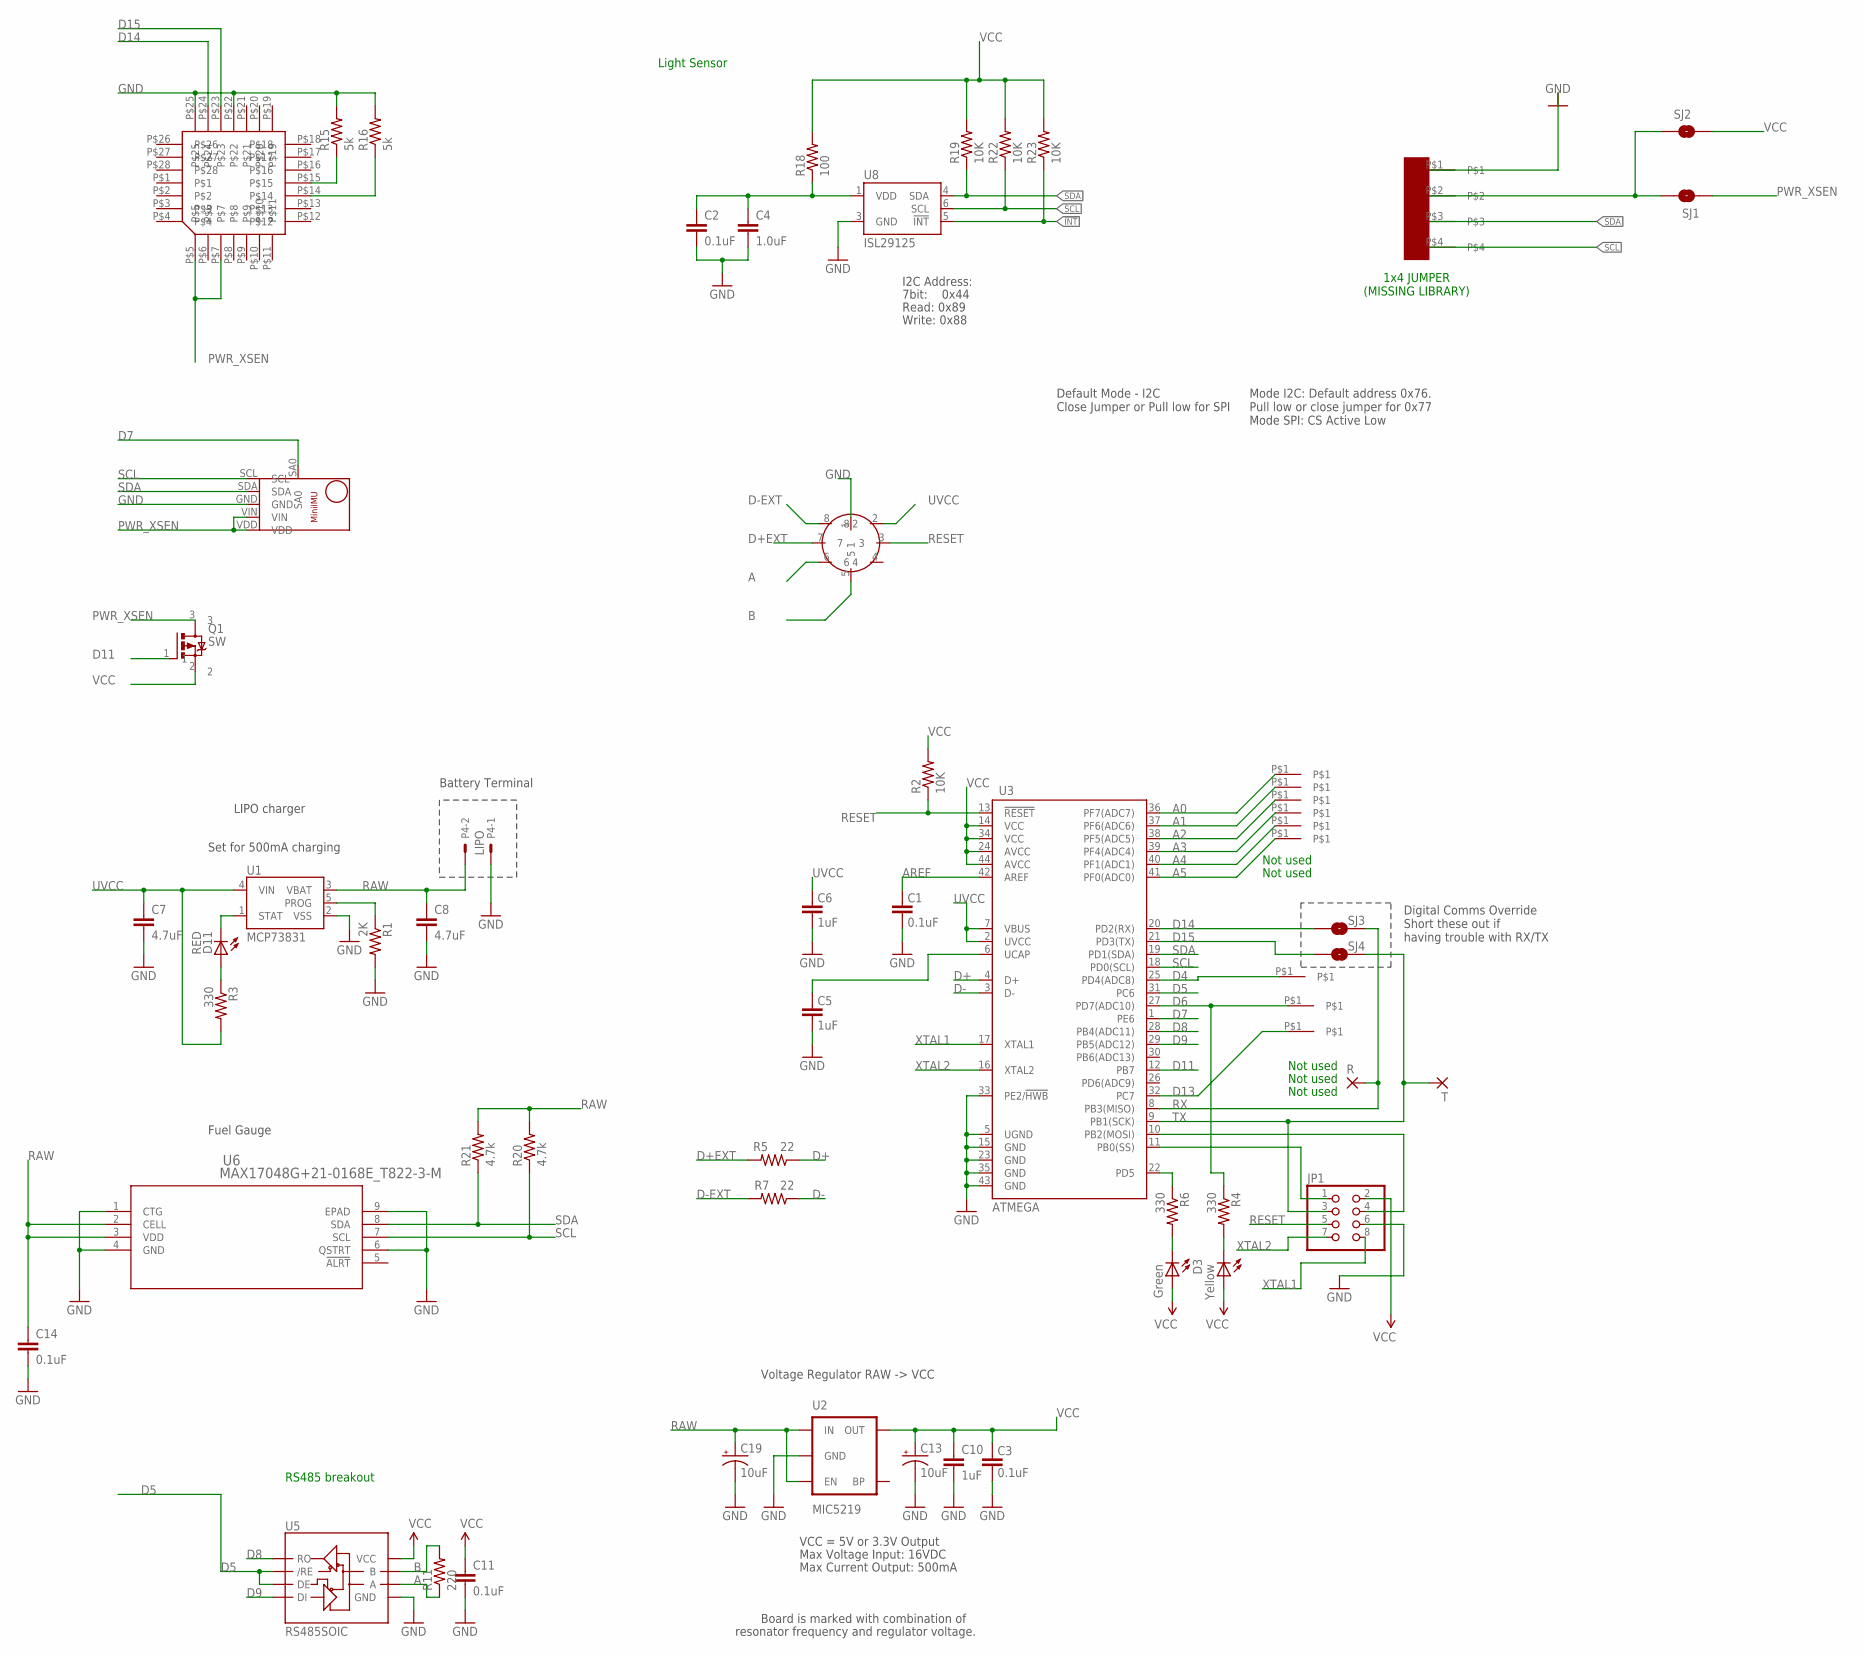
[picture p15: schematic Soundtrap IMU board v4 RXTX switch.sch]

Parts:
C1, C2, C3: 0.1uF; 0603-CAP
C4: 1.0uF; 0603-CAP
C5, C6, C10: 1uF; 0603-CAP
C7, C8: 4.7uF; 0402-CAP
C11, C14: 0.1uF; 0402-CAP
C13, C19: 10uF; EIA3216
D1: Yellow; LED-0603
D3: Green; LED-0603
D11: RED; LED-0603
JP1: PINHD-2X4; 2X04
P1: SUBCON_MICRO_8_EDGE_ORDERED; SUBCON_MICRO_8_EDGE
P2: MINI_IMU
P3: EXT_PRES
P4: LIPO; 22-23-2021
Q1: SW; SOT23
R: 1,6/0,9
R1: 2K; 0402-RES
R2, R19, R22, R23: 10K; 0603-RES
R3: 330; 0402-RES
R4, R6: 330; 0603-RES
R5, R7: 22; 0603-RES
R11: 220; 0402-RES
R15, R16: 5k; R0603
R18: 100; 0603-RES
R20, R21: 4.7k; 0402-RES
SJ1, SJ3, SJ4: SJ1; SJ_2S-NO
SJ2: 3v3; SJ_2S-NO
T: 1,6/0,9
U1: MCP73831; SOT23-5
U2: MIC5219; SOT23-5
U3: ATMEGA; QFN-44-NOPAD_1:1-OUTFAKES
U5: RS485SOIC; SO08
U6: MAX17048G+21-0168E_T822-3-M; 21-0168E_T822-3-M
U7: XSENSE; MC-28PLCC-SMT
U8: ISL29125; ODFN-LD-6
U$5: D4; TEST_POINT
U$6, U$7, U$8, U$9, U$10, U$11, U$12, U$13: TEST_POINT

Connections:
!INT: R23.1, U8.5 (!INT)
A: P1.6, R11.1, U5.6 (A)
A0: U3.36 (PF7(ADC7)), U$8.P$1
A1: U3.37 (PF6(ADC6)), U$9.P$1
A2: U3.38 (PF5(ADC5)), U$10.P$1
A3: U3.39 (PF4(ADC4)), U$11.P$1
A4: U3.40 (PF1(ADC1)), U$12.P$1
A5: U3.41 (PF0(ADC0)), U$13.P$1
AREF: C1.2, U3.42 (AREF)
B: P1.5, R11.2, U5.7 (B)
D4: U3.25 (PD4(ADC8)), U$5.P$1
D5: U3.31 (PC6), U5.2 (/RE), U5.3 (DE)
D6: R4.1, U3.27 (PD7(ADC10)), U$6.P$1
D7: P2.SA0, U3.1 (PE6)
D8: U3.28 (PB4(ADC11)), U5.1 (RO)
D9: U3.29 (PB5(ADC12)), U5.4 (DI)
D11: Q1.1, U3.12 (PB7)
D13: U3.32 (PC7), U$7.P$1
D14: SJ3.2, U3.20 (PD2(RX)), U7.P$24
D15: SJ4.2, U3.21 (PD3(TX)), U7.P$23
D+: R5.1, U3.4 (D+)
D+EXT: P1.7, R5.2
D-: R7.1, U3.3 (D-)
D-EXT: P1.8, R7.2
EXT_PRES_POW: P3.P$2, SJ1.2, SJ2.1
GND: C1.1, C2.2, C3.1, C4.2, C5.1, C6.1, C7.2, C8.2, C10.2, C11.2, C13.C (-), C14.2, C19.C (-), JP1.6, P1.1, P2.GND, P3.P$1, P4.1, R1.2, R15.2, R16.2, U1.2 (VSS), U2.2 (GND), U3.5 (UGND), U3.15 (GND), U3.23 (GND), U3.33 (PE2/!HWB), U3.35 (GND), U3.43 (GND), U5.5 (GND), U6.1 (CTG), U6.4 (GND), U6.6 (QSTRT), U6.9 (EPAD), U7.P$22, U7.P$25, U8.3 (GND)
MISO: JP1.1, U3.11 (PB0(SS))
MOSI: JP1.4, U3.10 (PB2(MOSI))
unnamed: C2.1, C4.1, R18.1, U8.1 (VDD)
unnamed: D11.A, R3.1
unnamed: C5.2, U3.6 (UCAP)
unnamed: D1.C, R4.2
unnamed: D3.C, R6.2
unnamed: R15.1, U7.P$15
unnamed: R16.1, U7.P$14
PROG: R1.1, U1.5 (PROG)
PWR_XSEN: P2.VDD, P2.VIN, Q1.3, SJ1.1, U7.P$5, U7.P$7
RAW: C8.1, C14.1, C19.A (+), P4.2, R20.2, R21.2, U1.3 (VBAT), U2.1 (IN), U2.3 (EN), U6.2 (CELL), U6.3 (VDD)
RESET: JP1.5, P1.3, R2.1, U3.13 (!RESET)
RX: R.1, SJ3.1, U3.8 (PB3(MISO))
SCL: P2.SCL, P3.P$4, R20.1, R22.1, U3.18 (PD0(SCL)), U6.7 (SCL), U8.6 (SCL)
SDA: P2.SDA, P3.P$3, R19.1, R21.1, U3.19 (PD1(SDA)), U6.8 (SDA), U8.4 (SDA)
STAT: D11.C, U1.1 (STAT)
TX: JP1.3, SJ4.1, T.1, U3.9 (PB1(SCK))
TXLED: R6.1, U3.22 (PD5)
UVCC: C6.2, C7.1, P1.2, R3.2, U1.4 (VIN), U3.2 (UVCC), U3.7 (VBUS)
VCC: C3.2, C10.1, C11.1, C13.A (+), D1.A, D3.A, JP1.2, Q1.2, R2.2, R18.2, R19.2, R22.2, R23.2, SJ2.2, U2.5 (OUT), U3.14 (VCC), U3.24 (AVCC), U3.34 (VCC), U3.44 (AVCC), U5.8 (VCC)
XTAL1: JP1.8, U3.17 (XTAL1)
XTAL2: JP1.7, U3.16 (XTAL2)

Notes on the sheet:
Max Voltage Input: 16VDC
Max Current Output: 500mA
Board is marked with combination of
resonator frequency and regulator voltage.
VCC = 5V or 3.3V Output
Not used
Set for 500mA charging
LIPO charger
Default Mode - I2C Close Jumper or Pull low for SPI
Mode I2C: Default address 0x76. Pull low or close jumper for 0x77 Mode SPI: CS Active Low
Light Sensor
RS485 breakout
7bit: 0x44
I2C Address:
Read: 0x89
Write: 0x88
1x4 JUMPER (MISSING LIBRARY)
Fuel Gauge
Battery Terminal
Digital Comms Override Short these out if having trouble with RX/TX
Voltage Regulator RAW -> VCC

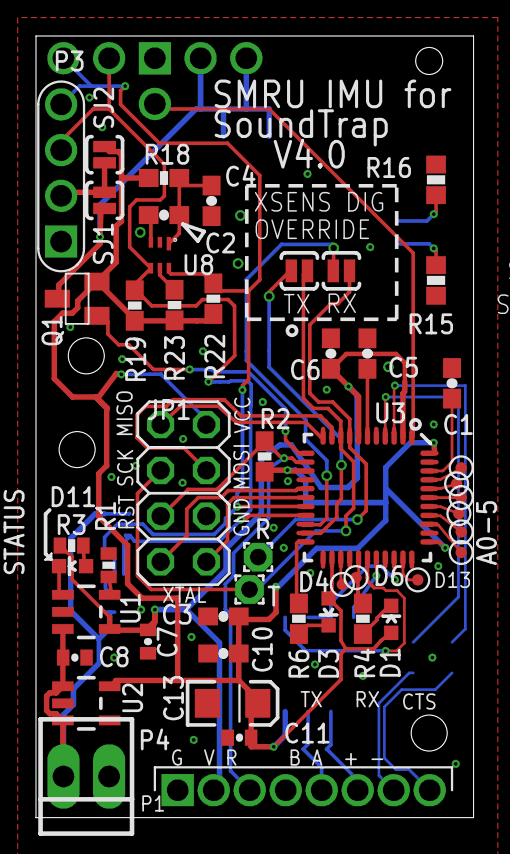
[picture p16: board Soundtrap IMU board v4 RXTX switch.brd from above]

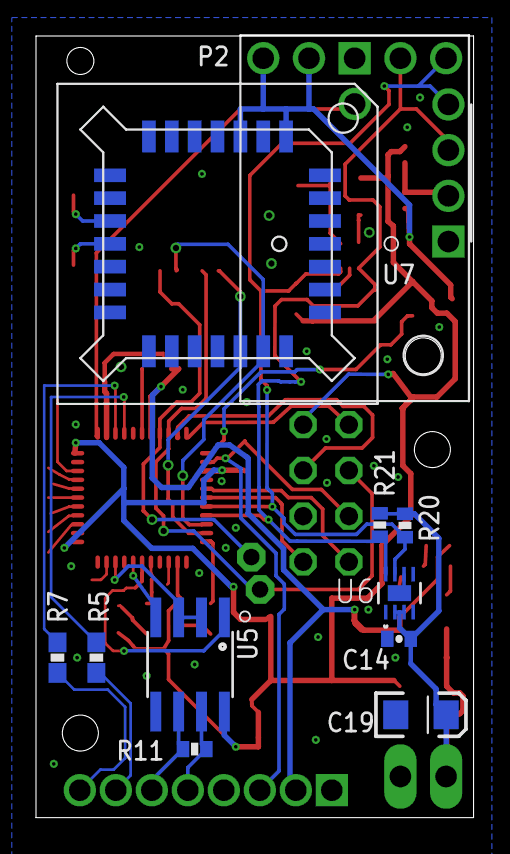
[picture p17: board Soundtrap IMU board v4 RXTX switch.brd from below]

Board: 2 copper layers, 24.3 x 43.4 mm, 60 parts (11 on the bottom side), 49 nets.

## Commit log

2021-12-22 Add particle filter code and housings
    [Trap frame with wider slots revE.stl, hydrophone brace revB.stl, positive model dual battery revD.stl]
2021-12-23 Updated directories
    [positive model dual battery revD.stl]
2022-01-07 Sensor package code
2022-01-10 Added sensor board files
    [ArduinoBoardGW_Final_IMU_updated BOM_3a.xlsx, Soundtrap IMU board v4 RXTX switch.brd, Soundtrap IMU board v4 RXTX switch.sch, Soundtrap IMU v4b BOM.xlsx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]
2026-05-26 Add buzz analysis MATLAB tools and data
    Introduce a new analysis/buzzes module for buzz and call analysis: adds multiple MATLAB functions (load_event_clicks, buzz2ici, matchbuzzes, matchbuzz2track, filtbuzzesQ, filtbuzzesevent, eventbuzzes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

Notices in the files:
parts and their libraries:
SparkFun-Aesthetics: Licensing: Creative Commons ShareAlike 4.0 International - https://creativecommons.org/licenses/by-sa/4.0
